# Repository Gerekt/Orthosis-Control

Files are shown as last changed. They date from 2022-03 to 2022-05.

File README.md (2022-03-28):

# Orthosis-Control
A Convolutional Neural Network powered control system for a hand orthosis/exoskeleton. 

This repository holds files related to a graduation assignment for the Saxion University of applied sciences.
The MSWC dataset is used in combination with the MobileNetV3 architecture for the CNN.

# Folder structure
The folders have the following purposes:

**Dataset**:                     Holds the dataset that is used. The dataset consits of certain parts/words of the MSWC dataset.

**On-device inference**:         Holds all the needed files for the inference that is used on the Raspberry Pi 4B. A trained model is also needed but not included

**Pre-processing&Training**:     Holds pre-processing scripts for the MSWC dataset and the notebook that is used for training the model.

**Trained models**:              Holds several pre-trained models.

# Setup guide
This guide will describe the process of running a pre-trained model onto a new Raspberry Pi 4B.
The following things are needed:
-Raspberry Pi 4B + USB-C power supply
-Minimum 16GB of storage, so either a flashdrive or SD card(Flashdrive preffered due to read-write cycles damaging SD card)
-Mini displayport -> HDMI/Displayport cable
-IQaudio Codec Zero ADC HAT
-Secondary monitor + Keyboard + Mouse for RPI

**Flashing image to Raspberry Pi**
We start by flashing an image which holds an OS to the Raspberry Pi. We will use an existing image which includes the TensorFlow library, which will make instalation easier.

Download the QEngineering 64-bit Raspberry Pi OS image: https://drive.google.com/file/d/1s8ulI44O96qmVPmWyz8yw3lzamh-32gN/view?usp=sharing

Download and install the image flasher: https://downloads.raspberrypi.org/imager/imager_latest.exe

Insert the storage device into your computer
Open the Raspberry Pi imager
Go to: Select OS, and scroll down and select the custom image file.



Select the recently downloaded QEngineering Raspberry Pi OS image, and press Open.

Lastly select the right storage device(which should be the inserted SD or flashdrive), and press the write button in the imager. 

Let the process finish, which will result in a flashed storage device.

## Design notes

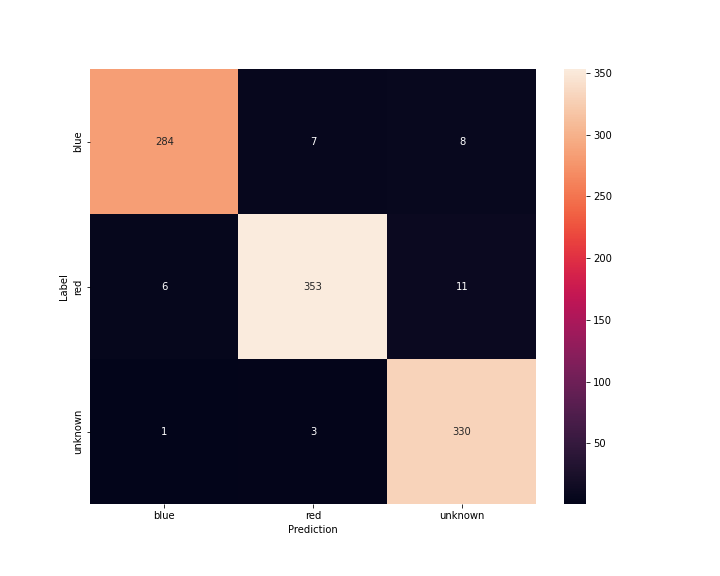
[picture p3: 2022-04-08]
Trained models/V5.0_simpleCNN_MSWC_blue-red-unknown_spectrogram_05-04-2022/metadata/confusion_matrix.png

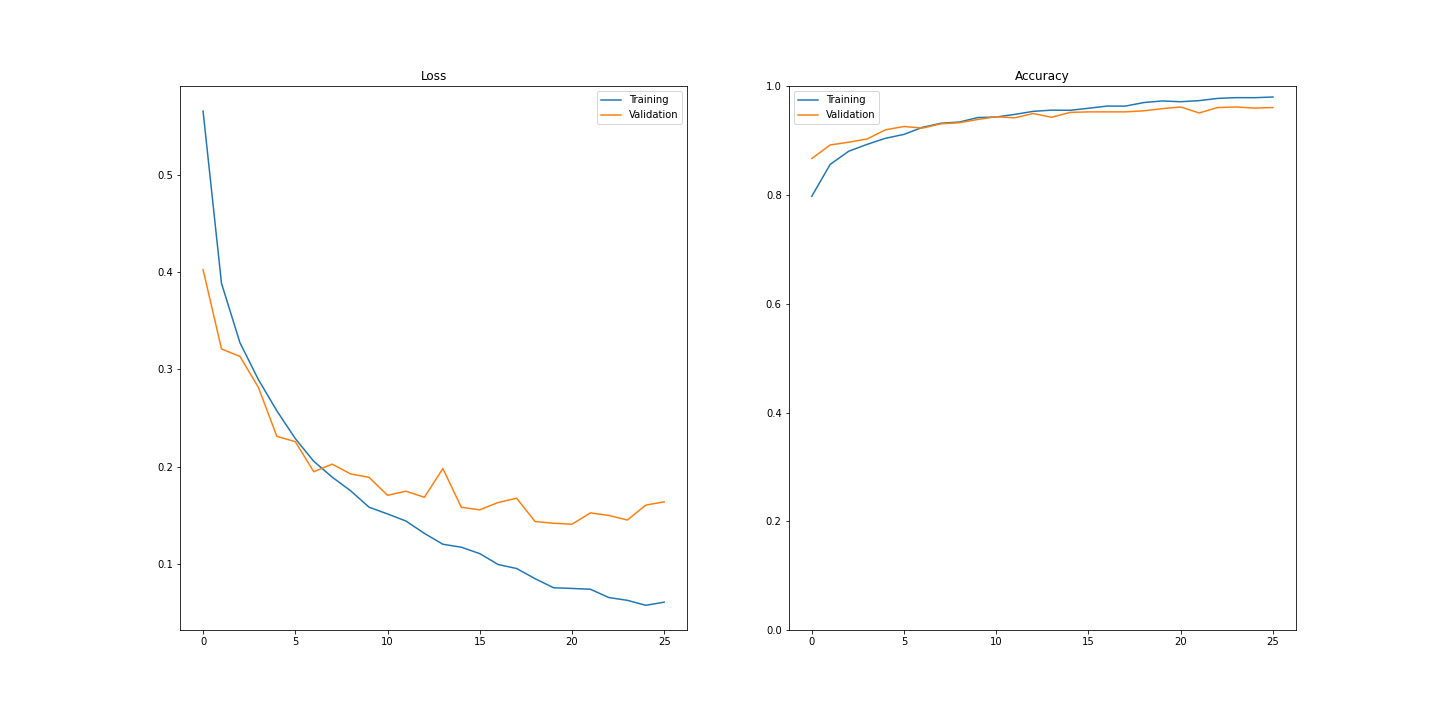
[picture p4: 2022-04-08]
Trained models/V5.0_simpleCNN_MSWC_blue-red-unknown_spectrogram_05-04-2022/metadata/training_graph.png

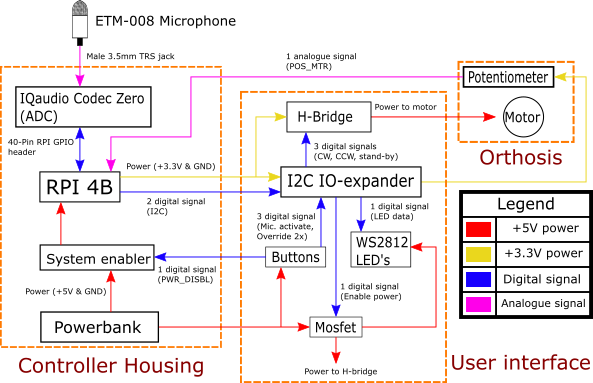
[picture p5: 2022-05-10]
Construction Files/Diagrams/Electronic Diagram(Technical).png

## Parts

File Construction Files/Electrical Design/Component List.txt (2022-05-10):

-------------------------------------------------------------------------------------------------------------
Nog te kopen

1x 3-pos, aan-neutraal-uit tuimelschakelaar: https://www.robotshop.com/be/nl/momentary-manual-dpdt-tuimelschakelaar.html
1x 2-pos, aan-uit tuimelschakelaar: https://www.kiwi-electronics.nl/nl/aan-uit-tuimelschakelaar-rood-3630?search=rocker
1x Drukknop met LED: https://www.kiwi-electronics.nl/nl/16mm-drukknop-met-led-puls-groen-2179
1x5 WS2812B 5mm LED's, 3 daadwerkelijk nodig: https://opencircuit.shop/product/NeoPixel-Diffused-5mm-Through-Hole-LED
3x LED Panel Houder/mount: https://www.tinytronics.nl/shop/nl/componenten/led's/accessoires/5mm-led-houder-metaal

1x TB6612 H-Bridge: https://www.kiwi-electronics.nl/nl/adafruit-tb6612-1-2a-dc-stepper-motor-driver-breakout-board-2188
1x I2C IO expander: https://www.tinytronics.nl/shop/nl/communicatie-en-signalen/io-converters/pcf8574-i2c-io-expander

3x Transistor NPN(general purpose): https://www.tinytronics.nl/shop/nl/componenten/transistoren/npn-transistor-2n3904 
2x Transistor MOSFET-N (Toggle power + motor/LEDS):https://www.kiwi-electronics.nl/nl/n-channel-power-mosfet-irlb8721-397?search=mosfet
8x Resistors (1x 5K, 3x 1K, 1x 10K, 1x 100, 2x 500): -
3x Diode: https://www.tinytronics.nl/shop/nl/componenten/diodes/diode-1n4007
2x Capacitor(Decouple): https://www.tinytronics.nl/shop/nl/componenten/condensatoren/100nf-50v-ceramische-condensator

1x Powerbank, elke powerbank >10.000mAH en meerdere poorten goed: https://www.mediamarkt.nl/nl/product/_hama-187261a-power-pack-pd10-hd-antraciet-1714846.html
1x Connector GX12-5 5-pin M+F: https://www.tinytronics.nl/shop/nl/kabels-en-connectoren/connectoren/gx/gx12/gx12-5-connector-set

2x1m Cable sleeve(To bundle outgoing cables), kon het niet vinden bij de andere winkels:https://nl.rs-online.com/web/p/cable-sleeves/0408209 
											https://www.123-3d.nl/123-3D-Vlechtkous-4-mm-zwart-1-meter-i5043-t13165.html
											 
1x Type C connector oplaad poort: https://opencircuit.shop/product/usb-2.0-type-c-connector-breakout-board
2x USB-C to loose wire stroomkabel(Powerbank -> oplaadpoort, Relay -> RPI): https://www.tinytronics.nl/shop/nl/kabels-en-connectoren/kabels-en-adapters/usb/usb-c/usb-c-stroomkabel-met-losse-draden-en-hoek-30cm?sort=p.price&order=ASC
2x USB-A Male connector(Output powerbank): https://www.tinytronics.nl/shop/nl/kabels-en-connectoren/connectoren/usb/usb-a-connector-diy-male

1x Raspberry Pi 4b(Gebruik nu eigen RPI): 
-------------------------------------------------------------------------------------------------------------
Al gekocht

1x Minimaal 16 GB storage (USB flashdrive(betere levensduur) of sd kaart(minder stroomverbruik))
1x IQaudIO CODEC Zero
1x ETM-008 Uni-directional microphone

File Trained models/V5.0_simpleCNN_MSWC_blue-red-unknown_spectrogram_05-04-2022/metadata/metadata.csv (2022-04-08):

ModelName | Test split accuracy | CNN | Dataset | TF_Version | Data augmentation percentage | Time shift percentage | Noise addition percentage | Noise SNR | Normalize Spectrogram | Sample Rate | Window length(Spectro) | Hop length(Spectro) | NFFT size | Epochs | Batch size | Comments
V5.0_simpleCNN_MSWC_blue-red-unknown_spectrogram_05-04-2022 | 0.9641076769690927 | simpleCNN | MSWC | 2.8.0 | 0.25 | 0.5 | 0.3 | 10 | False | 16000 | 256 | 128 | 256 | 60 | 64 | Normal 1D spectrogram 129x124, from_logits=True in sparsecatagoricalAccuracy

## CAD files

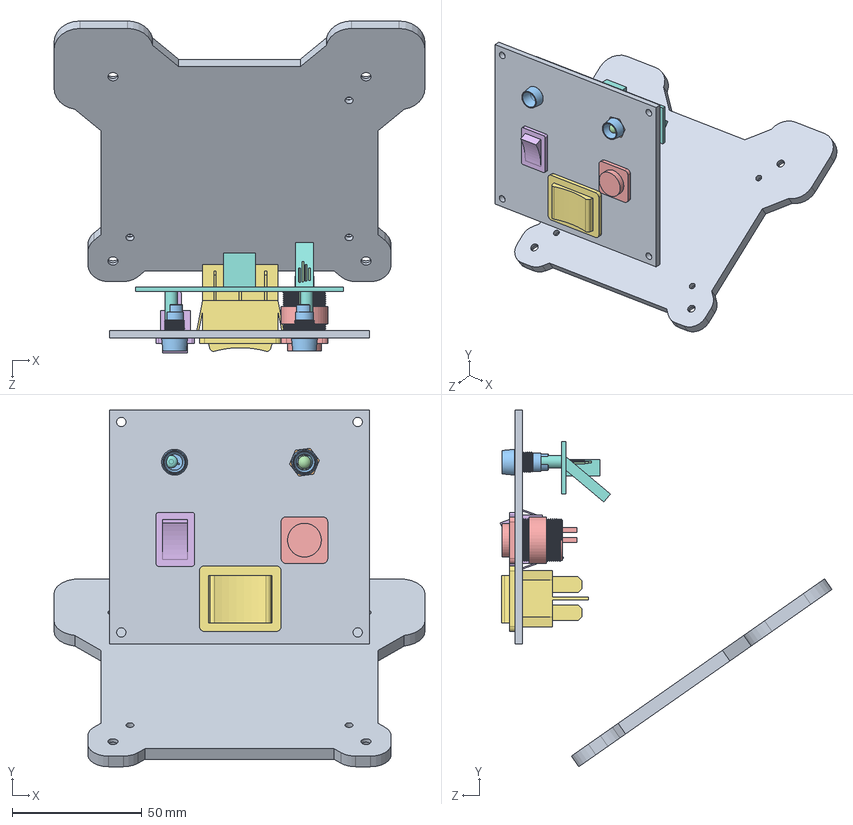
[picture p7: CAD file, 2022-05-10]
Construction Files/CAD/User Interface Panel + Walls.SLDASM
142.8 x 137.2 x 127.8 mm
Enclosure Interface panel FRONT
GrundkÃ¶rper v7.iges x 2
16mm Push Button Kiwi
RockerSwitch On_Off Kiwi
Double Throw Rocker Switch Forward_off_Backward
LED interface board
Enclosure User Interface Base

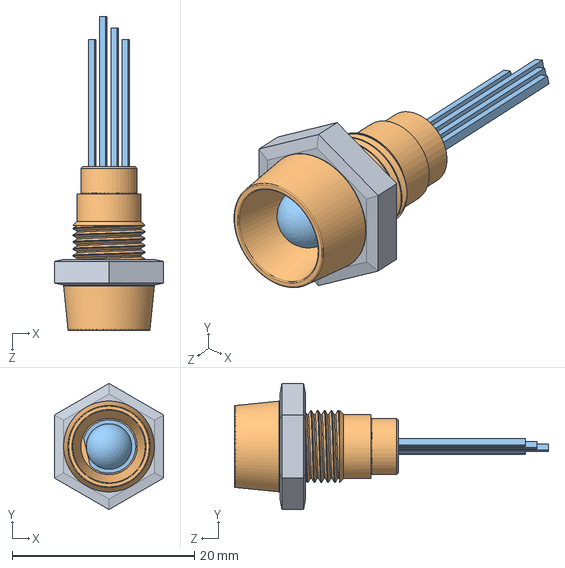
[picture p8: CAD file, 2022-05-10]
Construction Files/CAD/Components/LED holder 5mm.SLDASM
12.0 x 13.9 x 34.5 mm
GrundkÃ¶rper v7.iges
5mm RGB LED

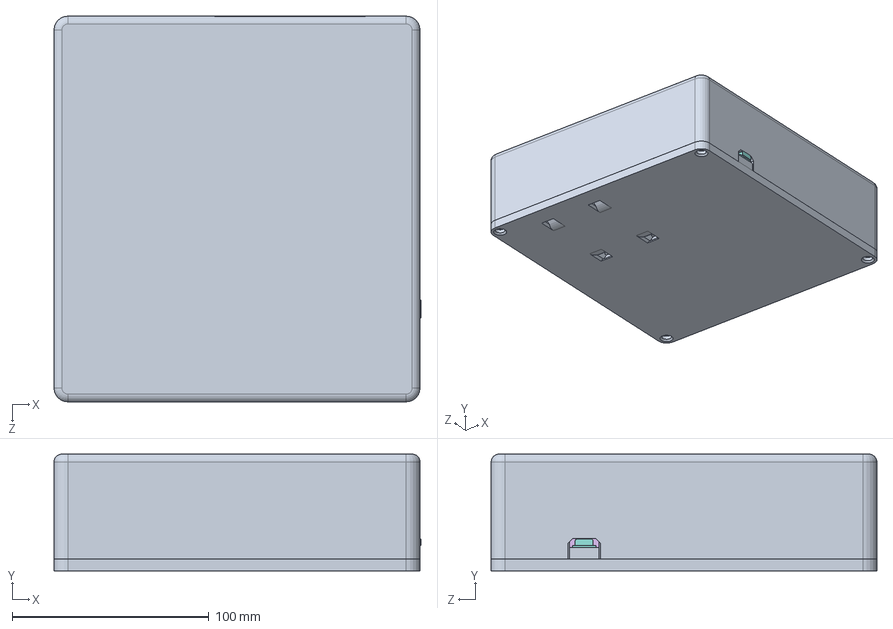
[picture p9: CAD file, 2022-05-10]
Construction Files/CAD/Control system enclosure.SLDASM
186.5 x 59.4 x 196.0 mm
Control system enclosure Base
PCB, RPi4ModelB
Broadcom BCM2711B0 CPU, RPi4ModelB
2.54 mm DUPONT MALE PIN HEADER, POE, 2X2, RPi4ModelB
2.54 mm DUPONT MALE PIN HEADER, IO, 2X20, RPi4ModelB
Camera Connector, RPi4ModelB
Microphone Plug, RPi4ModelB
Display Connector, RPi4ModelB
Gigabit Ethernet Port, RPi4ModelB
Female Micro HDMI Connector, RPi4ModelB x 2
Female USB Type C Connector, RPi4ModelB
2X USB3.0 PORTS, RPi4ModelB
91D77 D9WHV 778K, 4 GB LPDDR4 SDRAM, RPi4ModelB
Cypress CYW43455 Wireless Module Cover, RPi4ModelB
SD Card Slot, RPi4ModelB
VIA VL805 PCIe USB 3.0 controller, RPi4ModelB
2X USB2.0 PORTS, RPi4ModelB
Broadcom BCM54213PE Gigabit Ethernet Transceiver, RPi4ModelB
MxL7704 Universal PMIC, RPi4ModelB
heat2 x 2
heat4
Hama PD10-HD powerbank
System enabler board
USB-C port
Control system enclosure Top

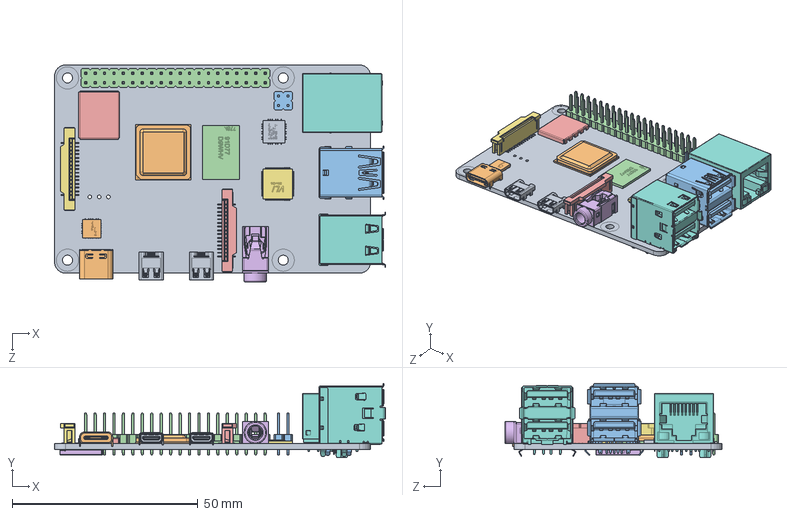
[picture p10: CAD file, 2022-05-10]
Construction Files/CAD/Components/Raspberry Pi 4b/Raspberry Pi 4 Model B.SLDASM
89.0 x 19.9 x 58.4 mm
PCB, RPi4ModelB
Broadcom BCM2711B0 CPU, RPi4ModelB
2.54 mm DUPONT MALE PIN HEADER, POE, 2X2, RPi4ModelB
2.54 mm DUPONT MALE PIN HEADER, IO, 2X20, RPi4ModelB
Camera Connector, RPi4ModelB
Microphone Plug, RPi4ModelB
Display Connector, RPi4ModelB
Gigabit Ethernet Port, RPi4ModelB
Female Micro HDMI Connector, RPi4ModelB x 2
Female USB Type C Connector, RPi4ModelB
2X USB3.0 PORTS, RPi4ModelB
91D77 D9WHV 778K, 4 GB LPDDR4 SDRAM, RPi4ModelB
Cypress CYW43455 Wireless Module Cover, RPi4ModelB
SD Card Slot, RPi4ModelB
VIA VL805 PCIe USB 3.0 controller, RPi4ModelB
2X USB2.0 PORTS, RPi4ModelB
Broadcom BCM54213PE Gigabit Ethernet Transceiver, RPi4ModelB
MxL7704 Universal PMIC, RPi4ModelB

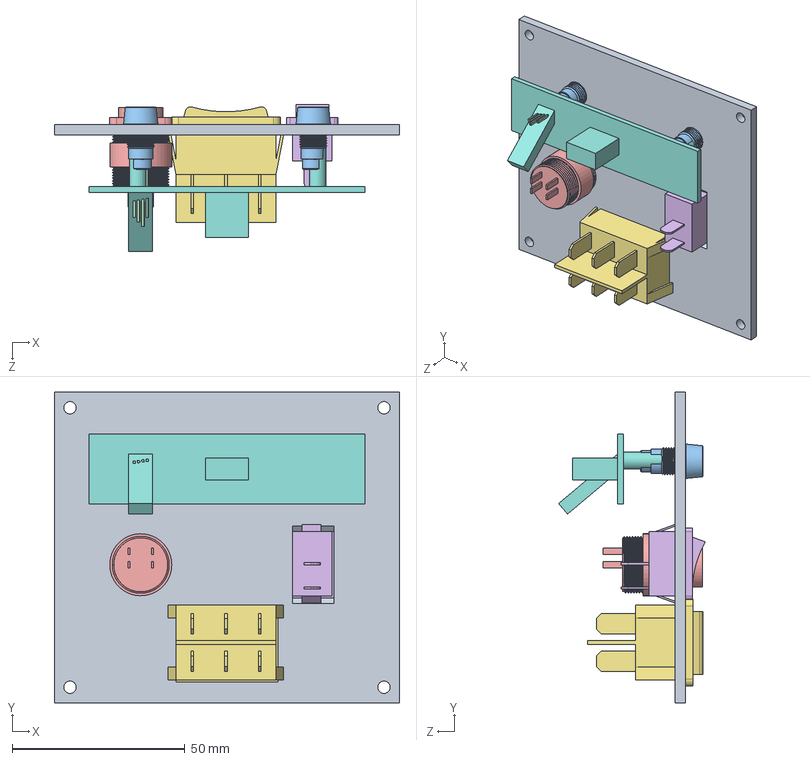
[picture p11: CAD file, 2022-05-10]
Construction Files/CAD/User interface Assembly.SLDASM
100.0 x 90.0 x 42.5 mm
Enclosure Interface panel FRONT
GrundkÃ¶rper v7.iges x 2
16mm Push Button Kiwi
RockerSwitch On_Off Kiwi
Double Throw Rocker Switch Forward_off_Backward
LED interface board

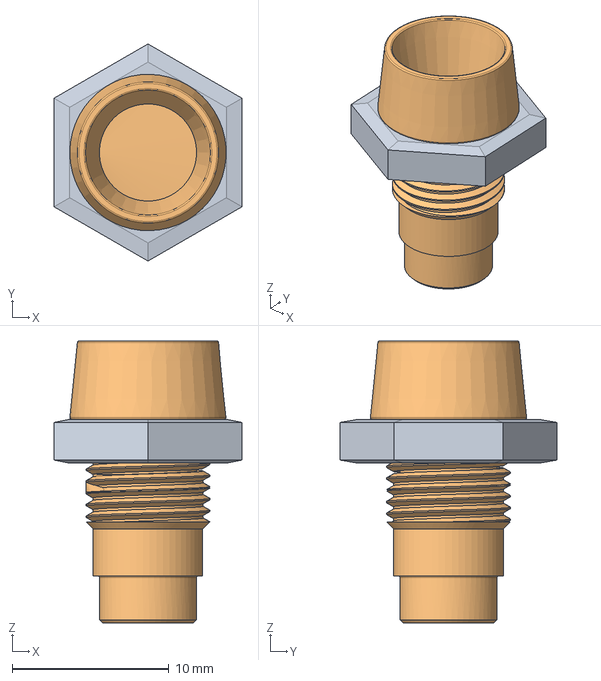
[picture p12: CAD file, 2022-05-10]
Construction Files/CAD/Components/5mm LED holder/LED holder 5mm.step
12.0 x 13.9 x 18.0 mm
M8 Kontermutter
Grundkörper

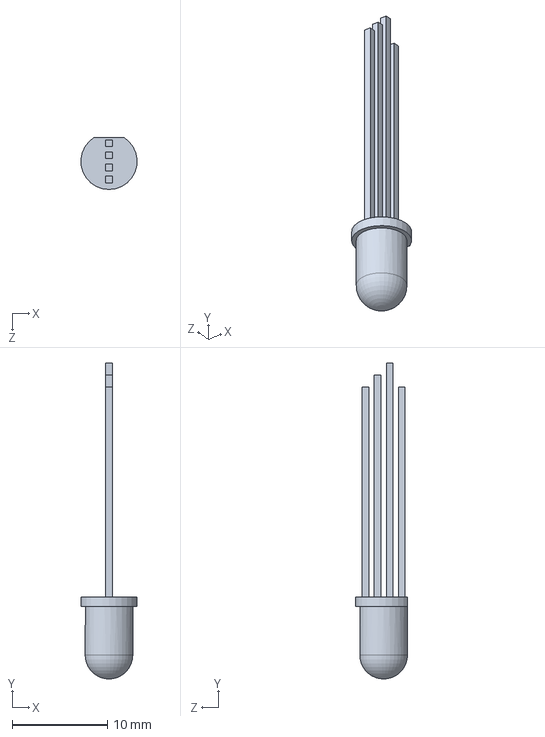
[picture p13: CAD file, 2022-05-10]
Construction Files/CAD/Components/5mm RGB LED.SLDPRT
5.88 x 33.1 x 5.45 mm

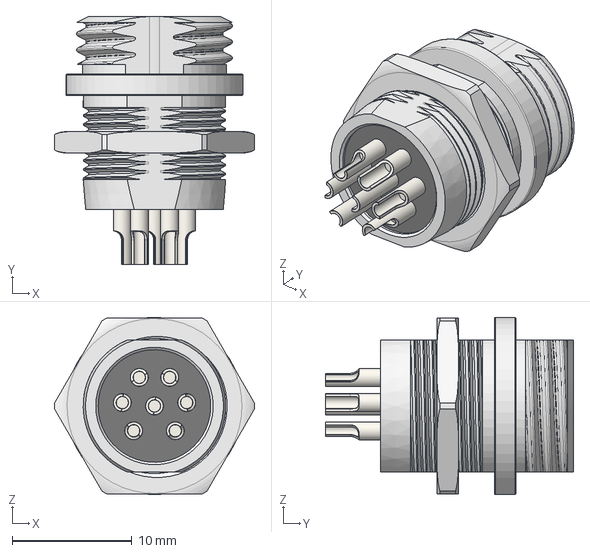
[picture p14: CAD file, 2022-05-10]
Construction Files/CAD/Components/GX-12 Connector/GX12-7P v2.step
16.7 x 20.7 x 14.8 mm

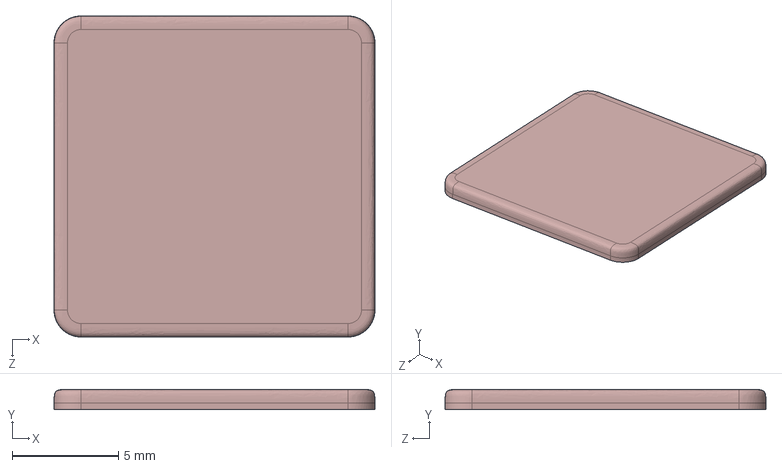
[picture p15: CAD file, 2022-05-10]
Construction Files/CAD/Components/Heatsink RPI/heat3.STEP
15.1 x 0.953 x 15.1 mm

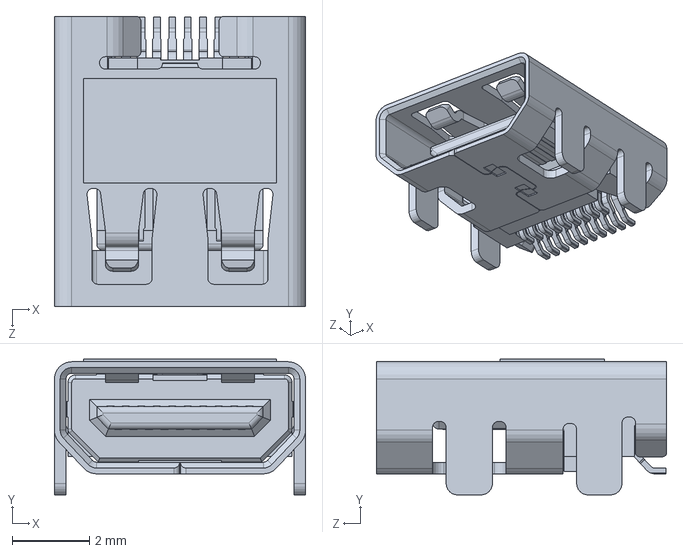
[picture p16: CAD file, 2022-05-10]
Construction Files/CAD/Components/Raspberry Pi 4b/Female Micro HDMI Connector, RPi4ModelB.SLDPRT
6.50 x 3.52 x 7.50 mm

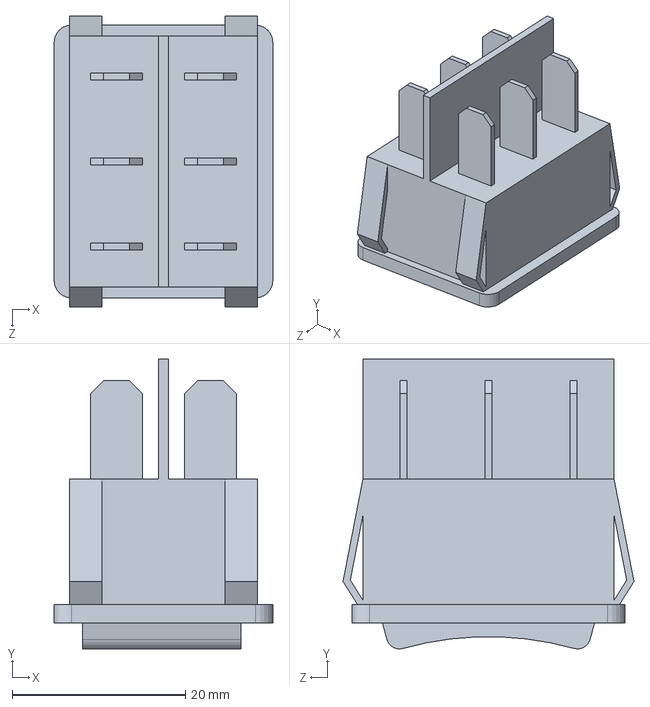
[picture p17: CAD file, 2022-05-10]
Construction Files/CAD/Components/Double Throw Rocker Switch Forward_off_Backward.SLDPRT
25.2 x 33.5 x 33.6 mm

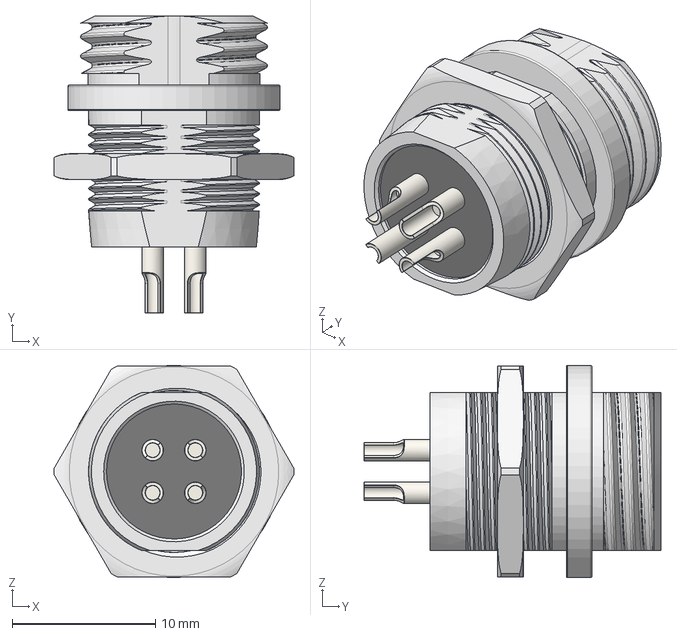
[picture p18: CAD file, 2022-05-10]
Construction Files/CAD/Components/GX-12 Connector/GX12-4P v3.step
16.7 x 20.7 x 14.8 mm

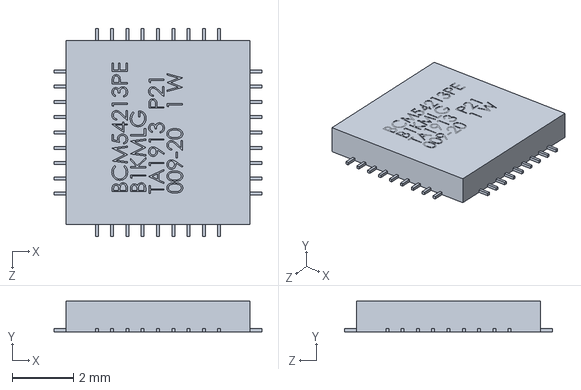
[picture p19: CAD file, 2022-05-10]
Construction Files/CAD/Components/Raspberry Pi 4b/Broadcom BCM54213PE Gigabit Ethernet Transceiver, RPi4ModelB.SLDPRT
6.80 x 1.00 x 6.80 mm

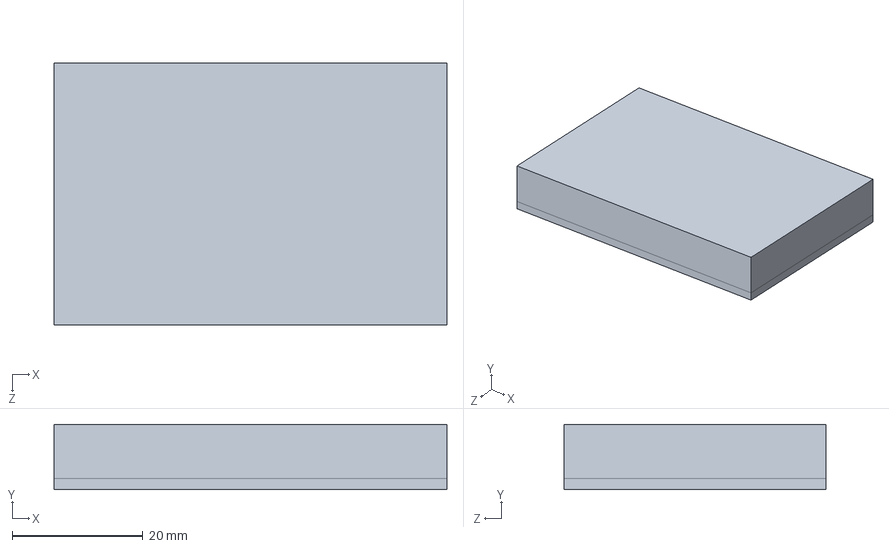
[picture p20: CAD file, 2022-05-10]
Construction Files/CAD/System enabler board.SLDPRT
60.1 x 10.0 x 40.1 mm

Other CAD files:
Construction Files/CAD/Components/GX-12 Connector/GX12-6P v2.step
Construction Files/CAD/Components/Raspberry Pi 4b/2.54 mm DUPONT MALE PIN HEADER, IO, 2X20, RPi4ModelB.SLDPRT
Construction Files/CAD/Components/16mm Push Button Kiwi.SLDPRT
Construction Files/CAD/Components/5mm LED holder/LED holder 5mm.iges
Construction Files/CAD/Components/GX-12 Connector/GX12-2P v2.f3d
Construction Files/CAD/Components/GX-12 Connector/GX12-2P v2.iges
Construction Files/CAD/Components/GX-12 Connector/GX12-2P v2.step
Construction Files/CAD/Components/GX-12 Connector/GX12-3P v2.f3d
Construction Files/CAD/Components/GX-12 Connector/GX12-3P v3.iges
Construction Files/CAD/Components/GX-12 Connector/GX12-3P v3.step
Construction Files/CAD/Components/GX-12 Connector/GX12-4P v3.f3d
Construction Files/CAD/Components/GX-12 Connector/GX12-4P v3.iges
Construction Files/CAD/Components/GX-12 Connector/GX12-5P v2.f3d
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

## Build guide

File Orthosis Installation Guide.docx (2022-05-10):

# iOrthosis-Control

A Convolutional Neural Network powered mobile control system for a hand orthosis/exoskeleton activated by voice commands. All running on a Raspberry Pi 4B.

This repository holds files related to a graduation assignment for the Saxion University of applied sciences. The MSWC dataset is used in combination with a simple CNN architecture.

# Folder structure

The folders have the following purposes:

Construction Files: Folder containing CAD files and electronic diagrams.

Custom dataset: Custom dataset containing several wavs of environmental sounds and conversations. Can be used to test the model after training. Additional wavs may also be added, although they need to be 16kHz .WAV files

Dataset MSWC: A pre-processed dataset containing the words: “red”& “blue”. The words are derived from selected words of the MSWC dataset. Link to entire dataset (https://mlcommons.org/en/multilingual-spoken-words/)

On-device inference: Holds all the needed files for the inference that is used on the Raspberry Pi 4B. A trained model is also needed for inference which is not included in this folder.

Pre-processing&Training: Holds pre-processing scripts for the MSWC dataset(MSWC_ds_PreProc) and the notebook that is used for training the model(modelTraining_ControlSystem). The opusdec.exe is also needed for the pre-processing of the dataset.

Trained models: Holds several pre-trained models. From V5.0 onwards the models also contain their performance data and metadata. This can be found inside of the model folder under “metadata” & “custom_dataset_results”. Currently V5.0 is meant to be used with the provided inference scripts. This model has one issue that it misclassifies silences as commands, due to no silences being included in the training.

# Setup RPI image

This guide will describe the process of running a pre-trained model onto a new Raspberry Pi 4B. The following things are needed:

- Raspberry Pi 4B + USB-C power supply
- Minimum 16GB of storage, so either a flashdrive or SD card(Flashdrive preferred due to read-write cycles damaging SD card)
- Mini displayport -> HDMI/Displayport cable
- IQaudio Codec Zero ADC HAT or another ADC for the microphone
- Secondary monitor + Keyboard + Mouse for RPI

Flashing image to Raspberry Pi We start by flashing an image which holds an OS to the Raspberry Pi. We will use an existing image which includes the TensorFlow library, which will make installation easier.

Download the QEngineering 64-bit Raspberry Pi OS image: https://drive.google.com/file/d/1s8ulI44O96qmVPmWyz8yw3lzamh-32gN/view?usp=sharing

or their GitHub: https://github.com/Qengineering/RPi-image

Download and install the image flasher:

https://downloads.raspberrypi.org/imager/imager_latest.exe

Insert the storage device into your computer. Open the Raspberry Pi imager, Go to: Select OS, and scroll down and select the custom image file.

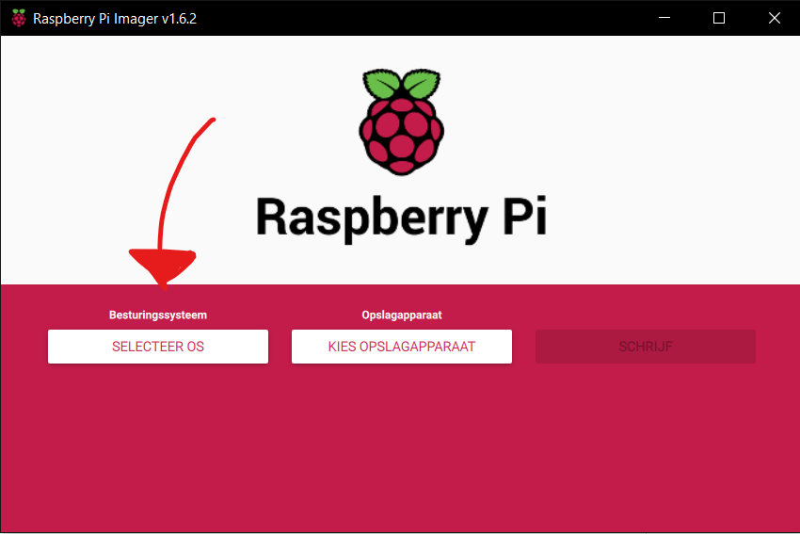
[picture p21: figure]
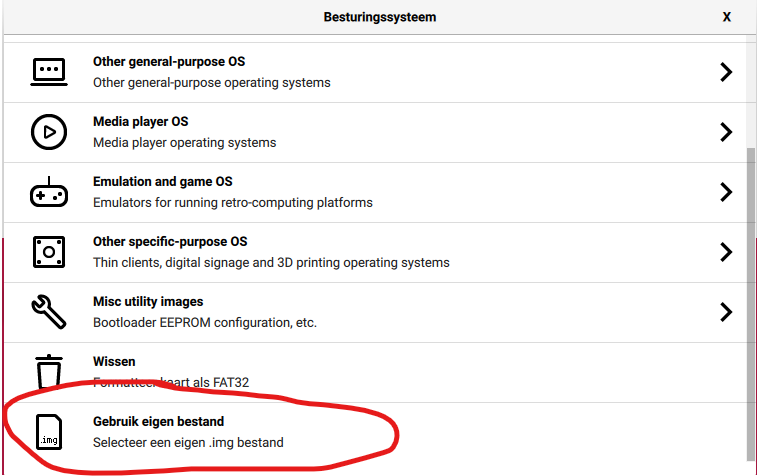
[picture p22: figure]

Select the recently downloaded QEngineering Raspberry Pi OS image, and press Open.

Select the right storage device(which should be the inserted SD or flashdrive).

Before flashing also press the cog icon after you have selected the OS file and storage device.

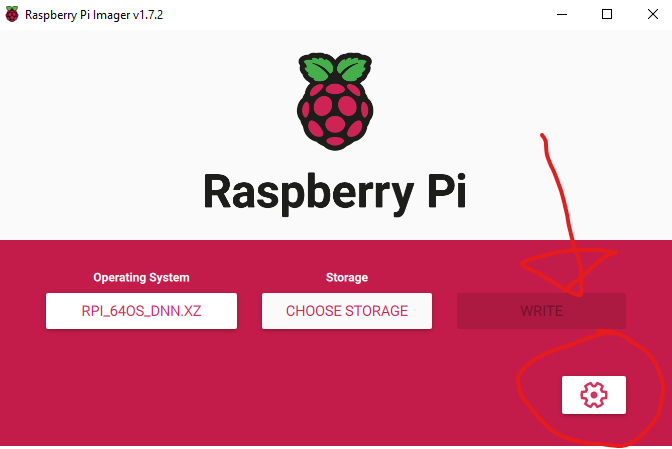
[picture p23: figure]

It will open up another window which allows the user to configure certain settings so that they do not need to be changed after flashing.

The hostname can be set to any hostname that is required, here I used “orthosis.local”, that means it can be found in the local network using that name.

SSH is also enabled, this will allow for accessing the raspberry pi using another computer and a program called Putty. You can then access the RPI via a terminal.

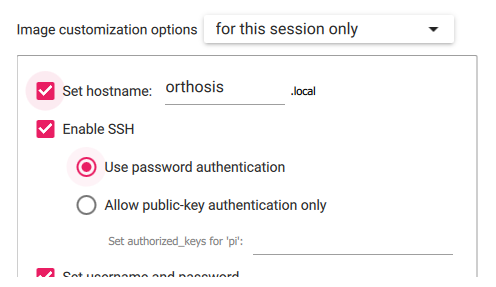
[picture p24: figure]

The password and username is also set. The password is currently set to “hankamp”.

The WiFi network is also configured. The name of the network needs to go at SSID. The password of the network should be entered at the password section.

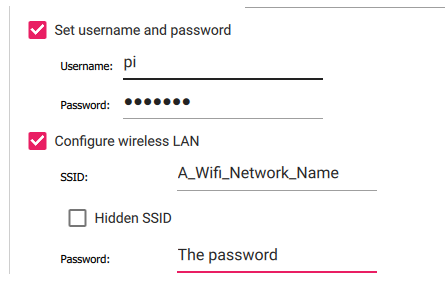
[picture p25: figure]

Lastly the locale settings need to be configured aswell. This ensures the right timezone and wifi settings. Here I used NL LAN county and Amsterdam timezone.

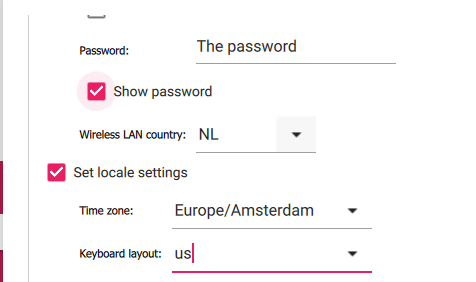
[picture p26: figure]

After the configuration press save, double check that you have the right storage device and press write.

This process might take a while.

Afterwards the SD card is flashed. Windows might ask if you want to reformat the drive. Do NOT do this, as it delete all the progress that is made thusfar.

# Putty guide

Instead of accessing the RPI by using a second monitor and peripherals. One can also access the RPI by using their main laptop/desktop. This can be done via SSH and a program called Putty. This will allow you to use your main computer for inputting commands to the RPI. This is not needed but may be more convenient.

You can download Putty here: https://www.chiark.greenend.org.uk/~sgtatham/putty/latest.html

Download and install the latest putty version for your machine.

After installing open putty, it will look similar to this.

For the hostname enter the hostname that was set during the configuration, so in my case that would be “orthosis.local”. Also add the user that you would like to log on as. So in this case the username is “pi”. Therefor the hostname will be: pi@orthosis or may also be pi@orthosis.local.

Additionally the IP may also be found via the RPI itself by typing “ifconfig” in a command window, or by looking at the router and the connected devices.

Your laptop/desktop will have to be on the same network as the RPI. This network will have to be the same one that was set during the configuration during the previous steps.

Give this configuration a name at the saved sessions. And press Save, this will allow for easier future access. After saving the configuration the connection can be established by pressing open.

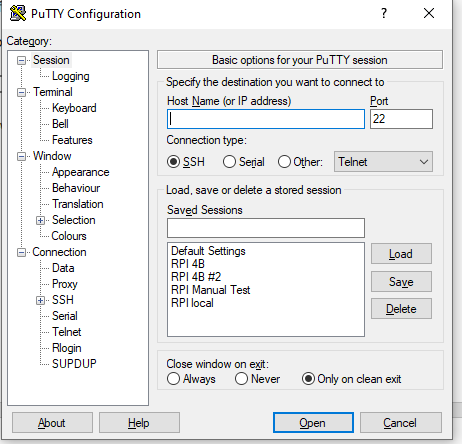
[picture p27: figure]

After opening the connection. Log in by using the password that was set, so “hankamp”. Now you can access the RPI via the command line terminal.

# Setup RPI settings

After flashing, the storage device can be inserted into the Raspberry Pi. Also connect the Raspberry to all the peripherals described in the previous chapter, such as the monitor. Also connect both HATs to the Raspberry Pi.

After connecting the peripherals connect the USB-C PSU to the Pi. Then login to the Raspberry Pi using the password: “3.14” or with “Hankamp” if the previous steps were followed.

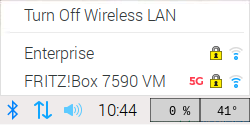
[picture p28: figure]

After logging in the Raspberry Pi will start up, this might take a while.

After starting the Raspberry Pi the WiFi may need to be manually enabled if this was not done correctly during the flashing of the SD card. To do this log in to the desired WiFi by clicking the symbol in the top right corner.

Press the button, after a while it shows the available networks, log into the desired network using the credentials.

Test if the WiFi has been correctly configured by opening the internet browser and going to a website.

If the Wi-Fi is set properly you can continue to the next step of the setup, which is needed for the HAT. Open a command prompt (Via SSH and Putty, or via a window on the RPI) and type the following line: “sudo raspi-config”

It will open the following screen.

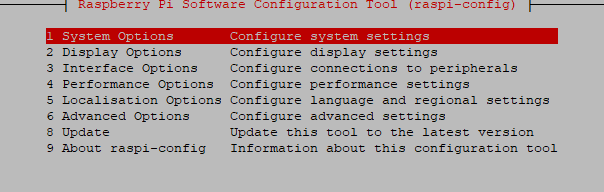
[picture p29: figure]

Go to interface (3) with the arrow keys and enable SPI and I2C by pressing enter. As can be seen on the following picture.

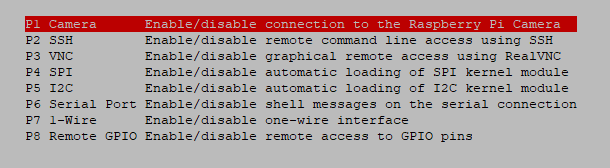
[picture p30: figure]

Now go back to the previous screen and go to the advance options (6). Then press enter on Expand Filesystem. This will make sure that the entire SD card is used for storage.

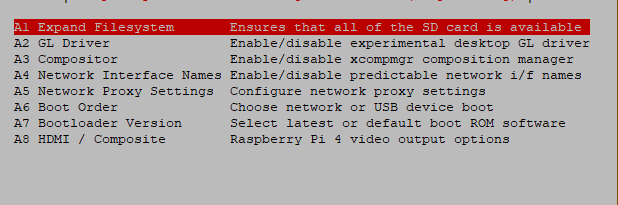
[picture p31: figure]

After this step go back to the previous screen and press finish. When asked to reboot press Yes. Otherwise type “sudo reboot now” Into the command line.

This will reboot the RPI and enable all the settings that were just configured.

Also update the current version by: “sudo apt-get update”

And “sudo apt-get upgrade” followed by “sudo reboot now”

After updating the settings, some additional settings need to be added for the HAT to work. This will be done by editing certain lines manually.

Type: “sudo nano ~/boot/config.txt”

Place an # before the line dtparam=audio=on, this will disable HDMI audio. Also add the following line under that one: “dtoverlay=iqaudio-codec”.

Save by pressing CTRL+X, and press enter.

# Cloning GitHub/Bitbucket repository

After configuring all the necessary settings, the code needs to be imported onto the Raspberry Pi. This will be done via Git. This step can only be completed if a working internet connection has been established on the RPI.

After the reboot that was done during the previous steps, log back into the RPI and open a new command line window.

Before being able to clone the repository you will need the link to the repository. Currently this is: https://github.com/Gerekt/Orthosis-Control.git

Now clone the repository by using the link.

Type: “sudo git clone https://github.com/Gerekt/Orthosis-Control.git”

The repository has now been cloned onto the RPI.

# Downloading Python libraries

The image that we used for the RPI already has several Python libraries pre-installed such as TensorFlow. However we need some additional libraries for the code.

First sounddevice: “python3 -m pip install sounddevice”

We cant install sounddevice easily as it needs portAudio to work, which is a C library. The only way to do this on a RPI with existing python modules is to manually compile the library with the following commands.

“cd ~” and “wget http://files.portaudio.com/archives/pa_stable_v190700_20210406.tgz”

“tar – xvzf pa_stable_v190700_20210406.tgz”

“sudo apt-get install libasound-dev”

“sudo apt-get install alsa-utils” And “sudo apt-get install mpg321”

“sudo apt-get install lame”

“cd portaudio” And “./configure && make”

“sudo make install” And “sudo ldconfig”

“sudo cp lib/.libs/libportaudio.a ~/Orthosis-Control/On-device inference/”

“sudo cp ~/portaudio/include/portaudio.h ~/Orthosis-Control/On-device\ inference/”

Now we have sounddevice and the C library. Next up Scipy. But first all the dependencies of scipy.

“sudo apt-get upgrade” and “sudo apt-get update”

“python3 -m pip install imutils” And “python3 -m pip install matplotlib”

“python3 -m pip install ipython” And “python3 -m pip install jupyter”

“python3 -m pip install sympy” and “python3 -m pip install nose”

Jupyter and Sympy may give errors when installing, during my installation this happened but did not matter for the installation of scipy.

“sudo apt install python3-gpiozero”

The last modules will take quite a long time, so be patient. (+20 min)

“python3 -m pip -vv install pandas” and “python3 -m pip -vv install numpy”

“python3 -m pip -vv install scipy”

# Testing configuration

Now we should have all the required libraries and files. We will test if everything is working by running the main control script. Go to it by: “cd ~/Orthosis-Control/On-device inference/”

And run the script with: “python3 ControlSystem.py”

After loading all the libraries it should start and give no library errors. It may give some errors related to the input device. This can be solved by running another script in the same folder. This script lists all the available input devices, the right one should be selected and copied into the main control system script.

Run the script with: “python3 audioListDevices.py”. The IQaudio microphone input should be the default.

Additional troubleshooting may be done with “arecord -l” and “arecord -L”, which lists all available devices.

And “sudo alsamixer”, which allows for changing certain parameters of the audio cards. Select the right card by pressing F6. Check if the microphones are enabled(Green box), if not enable or increase the gain by pressing “M” and the arrow keys respectively.

# Problems/Improvements

This chapter will summarize potential improvements that could be made and also the problems that the system currently has. If possible, solutions will also be provided that may solve the problem.

## Software

Problem | Type | Description | Solution
Models not trained with silences | Problem | The models are not trained with samples of silences and therefore misclassify silent audio as commands. | Add training silent training samples to unknown class or add new class containing silences and light noise.
Electronic peripherals not used | Improvement | The peripherals (LED’s, IO expander, and power button) are not used in the software | Add functionality into code.
Control script stops after 20sec | Improvement | The main script ControlSystem.py stops after 20sec. It stops as this made troubleshooting easier | Easier solution is to remove the 20 second variable in the loop to make it run indefinitely. May also add start stop capability to script, meaning that the classes get deleted and loaded again when the microphone activation button is pressed.
Device ID of IQAudio ADC can change | Improvement | The Device ID of the input devices of the IQAudio HAT can change after reboots. Which will result in no captured audio in the main control script. | Change HAT with USB ADC as the HAT is difficult to setup and troubleshoot. An USB ADC that is supported by the RPI may give better results.
TensorFlowLite capability | Improvement | The script currently uses the TensorFlow library and a TenserFlowLite model. This works fine but fully using TensorFlowLite as the library will give better performance. | Change TensorFlow library with TensorFlowLite. Will require slight reformatting of the code in the main script and wavToSpectrogram.py. Should be possible as no TensorFlow function is needed anymore.

## Mechanical

Problem | Type | Description | Solution
Sluggish case design | Improvement | The cases for the control system and user interface are big, bulky and heavy. They can be shrunk in size drastically. | Remodel both cases and print using less layers/walls. The models currently have a lot of empty space.
No aux passthrough | Improvement | The AUX cable from the microphone needs to go into the case, currently this results in a hole in the wall of the case. | Add an AUX passthrough where the user can plugin the microphone. The passthrough is fixed into the walls of the case. will then be connected to the ADC.
No analog inputs | Problem | The RPI does not have any analog inputs, but one is needed for the motor position | An I2C ADC can be added in the user interface, like for example the AD7992. Alternatively the motor position may be discarded, I.E. not be used.
Heat/cooling | Problem | The RPI gets very hot after a while. The HAT’s restrict airflow. | Add a special cooling case made of metal. A cooling fan may also be added. A sleeker HAT will also improve cooling.

## Electrical

Problem | Type | Description | Solution
System enabler | Improvement | System enabler is not implemented. System can therefor not be automatically shutdown | Select the right MOSFETS and rebuild the enabler board.
Cables | Improvement | Cables inbetween cases currently uses individual cables and are not long enough. | Rewire with cable with multiple strands like an ethernet cable.

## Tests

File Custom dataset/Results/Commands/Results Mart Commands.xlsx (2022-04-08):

MTestOG1(Quick) | Column1 | Column2 | Column3 | Column4 | Column5 | Column6 | Column7 | Column8 | Column9 | Column10 | Column11 | Column12 | Column13 | Column14 | Column15 | Column16 | Column17 | Column18 | Column19 | Column20 | Column21 | Column22 | Column23 | Column24 | Column25 | Column26 | Column27 | Column28 | Column29 | Column30 | Column31 | Column32 | Column33 | Column34 | Column35 | Column36 | Column37 | Column38 | Column39 | Column40 | Column41 | Column42 | Column43 | Column44 | Column45 | Column46 | Column47 | Column48 | Column49 | Column50 | Column51 | Column52 | Column53 | Column54 | Column55 | Column56 | Column57 | Column58 | Column59
Time of detected command(seconds): | 1.0 | 1.5 | 2.0 | 2.5 | 3.0 | 3.5 | 4.5 | 5.0 | 6.5 | 7.0 | 8.0 | 8.5 | 9.0 | 10.0 | 10.5 | 11.0 | 11.5 | 12.0 | 13.0 | 13.5 | 14.0 | 14.5 | 15.0 | 16.0 | 16.5 | 17.5 | 18.0 | 19.0 | 19.5 | 20.0 | 20.5 | 21.0 | 21.5 | 22.0 | 22.5 | 23.0 | 23.5 | 24.0 | 25.0 | 25.5 | 26.0 | 27.0 | 27.5 | 28.0 | 28.5 | 29.0 | 29.5 | 30.5 | 31.0 | 31.5 | 32.0 | 32.5 | 33.0 | 33.5 | 34.0 | 34.5 | 35.5 | 36.0 | 36.5
Detected command: | red | blue | blue | red | red | red | red | red | blue | blue | red | red | red | red | blue | blue | red | blue | blue | red | red | blue | blue | red | blue | red | blue | red | red | red | red | red | red | red | red | blue | red | blue | red | blue | red | red | blue | blue | blue | red | red | red | blue | blue | red | red | red | red | blue | blue | blue | blue | red
MTestOG2(Slow) | Column2 | Column3 | Column4 | Column5 | Column6 | Column7 | Column8 | Column9 | Column10 | Column11 | Column12 | Column13 | Column14 | Column15 | Column16 | Column17 | Column18 | Column19 | Column20 | Column21 | Column22 | Column23 | Column24 | Column25 | Column26 | Column27 | Column28 | Column29 | Column30 | Column31 | Column32 | Column33 | Column34 | Column35 | Column36 | Column37 | Column38 | Column39 | Column40 | Column41 | Column42 | Column43 | Column44 | Column45 | Column46 | Column47
Time of detected command(seconds): | 1.0 | 1.5 | 2.0 | 2.5 | 3.0 | 3.5 | 4.0 | 5.0 | 5.5 | 6.0 | 6.5 | 7.0 | 7.5 | 8.0 | 8.5 | 9.0 | 9.5 | 10.0 | 10.5 | 11.0 | 11.5 | 12.0 | 12.5 | 13.0 | 13.5 | 14.0 | 14.5 | 15.0 | 15.5 | 16.0 | 16.5 | 17.0 | 17.5 | 18.0 | 18.5 | 19.0 | 20.0 | 20.5 | 21.0 | 21.5 | 22.0 | 23.0 | 23.5 | 24.0 | 25.5 | 26.0
Detected command: | blue | blue | blue | blue | blue | red | blue | blue | red | blue | red | red | red | blue | blue | blue | red | red | red | blue | blue | blue | red | blue | red | blue | blue | red | red | blue | red | red | red | blue | red | red | blue | blue | blue | red | blue | blue | red | red | red | blue
MTest1(Quick) | Column2 | Column3 | Column4 | Column5 | Column6 | Column7 | Column8 | Column9 | Column10 | Column11 | Column12 | Column13 | Column14 | Column15 | Column16 | Column17 | Column18 | Column19
Time of detected command(seconds): | 5.0 | 7.0 | 10.0 | 13.0 | 20.5 | 22.5 | 27.0 | 29.5 | 32.5 | 36.5 | 38.0 | 39.5 | 42.0 | 44.0 | 44.5 | 46.5 | 56.0 | 61.5
Detected command: | red | red | red | blue | blue | blue | red | red | red | red | red | blue | blue | red | red | red | red | red
Mtest2(Slow) | Column2 | Column3 | Column4 | Column5 | Column6 | Column7 | Column8 | Column9 | Column10 | Column11 | Column12 | Column13 | Column14 | Column15 | Column16 | Column17 | Column18 | Column19 | Column20 | Column21
Time of detected command(seconds): | 3.5 | 5.0 | 7.0 | 9.0 | 10.0 | 13.0 | 20.5 | 22.0 | 27.0 | 29.5 | 32.5 | 36.5 | 38.0 | 39.5 | 42.0 | 44.0 | 44.5 | 46.5 | 56.0 | 61.5
Detected command: | red | red | red | red | red | blue | blue | blue | red | red | red | red | red | blue | blue | red | red | red | red | red
Mtest3(Quick) | Column2 | Column3 | Column4 | Column5 | Column6 | Column7 | Column8 | Column9 | Column10 | Column11 | Column12 | Column13 | Column14
Time of detected command(seconds): | 5.5 | 20.5 | 22.5 | 29.5 | 32.5 | 36.5 | 38.0 | 42.0 | 44.0 | 44.5 | 46.5 | 56.0 | 61.5
Detected command: | blue | blue | blue | red | red | red | red | blue | red | red | red | red | red
True labels (Quick) | Column2 | Column3 | Column4 | Column5 | Column6 | Column7 | Column8 | Column9 | Column10 | Column11 | Column12 | Column13 | Column14 | Column15 | Column16 | Column17 | Column18 | Column19 | Column20 | Column21 | Column22 | Column23 | Column24 | Column25 | Column26 | Column27 | Column28 | Column29 | Column30 | Column31 | Column32 | Column33 | Column34
Start + stop command: | 3.1 | 4.4 | 5.9 | 7.2 | 8.5 | 11.5 | 13.2 | 14.6 | 16 | 17.6 | 19 | 20.4 | 21.9 | 23.4 | 24.9 | 26.2 | 28.9 | 30.3 | 31.8 | 33.4 | 34.8 | 36.1 | 37.5 | 39 | 40.2 | 41.7 | 43.9 | 46 | 48 | 50.3 | 52.2 | 55.2 | 58.7
Spoken command: | red | red | Blue | red | red | Blue | red | blue | blue | blue | red | red | red | blue | blue | red | red | blue | red | blue | blue | red | red | blue | blue | blue | red | red | blue | blue | red | red | blue
True labels (Slow) | Column2 | Column3 | Column4 | Column5 | Column6 | Column7 | Column8 | Column9
Start + stop command: | 3.5 | 6.3 | 9.4 | 12.4 | 15.4 | 18.5 | 21.4 | 23.6
Spoken command: | Blue | Red | red | Blue | Blue | red | Blue | Red
Mtest4(Slow) | Column2 | Column3 | Column4 | Column5 | Column6 | Column7 | Column8 | Column9 | Column10 | Column11 | Column12 | Column13 | Column14
Time of detected command(seconds): | 5.5 | 20.5 | 22.5 | 29.5 | 32.5 | 36.5 | 38.0 | 42.0 | 44.0 | 44.5 | 46.5 | 56.0 | 61.5
Detected command: | blue | blue | blue | red | red | red | red | blue | red | red | red | red | red
Mtest5(Quick) | Column2 | Column3 | Column4 | Column5 | Column6 | Column7 | Column8 | Column9 | Column10 | Column11 | Column12 | Column13 | Column14 | Column15 | Column16 | Column17 | Column18 | Column19 | Column20 | Column21 | Column22 | Column23 | Column24 | Column25 | Column26 | Column27 | Column28 | Column29 | Column30 | Column31 | Column32 | Column33 | Column34 | Column35
Time of detected command(seconds): | 3.5 | 4.5 | 5.0 | 7.0 | 8.0 | 9.0 | 10.0 | 13.0 | 15.0 | 16.0 | 22.0 | 27.0 | 29.0 | 29.5 | 30.5 | 32.5 | 33.5 | 34.0 | 36.5 | 37.5 | 38.0 | 39.0 | 39.5 | 42.0 | 44.0 | 44.5 | 46.0 | 46.5 | 48.5 | 52.5 | 53.0 | 56.0 | 56.5 | 61.5
Detected command: | red | red | red | red | red | red | red | blue | blue | blue | blue | red | red | red | red | red | red | blue | red | red | red | red | blue | blue | red | red | red | red | blue | red | red | red | red | red
Mtest6(Slow) | Column2 | Column3 | Column4 | Column5 | Column6 | Column7 | Column8 | Column9 | Column10 | Column11 | Column12 | Column13 | Column14 | Column15 | Column16 | Column17 | Column18 | Column19 | Column20 | Column21 | Column22 | Column23 | Column24 | Column25 | Column26 | Column27 | Column28 | Column29 | Column30 | Column31 | Column32 | Column33 | Column34 | Column35
Time of detected command(seconds): | 3.5 | 4.5 | 5.0 | 7.0 | 8.0 | 9.0 | 10.0 | 13.0 | 15.0 | 16.0 | 22.0 | 27.0 | 29.0 | 29.5 | 30.5 | 32.5 | 33.5 | 34.0 | 36.5 | 37.5 | 38.0 | 39.0 | 39.5 | 42.0 | 44.0 | 44.5 | 46.0 | 46.5 | 48.5 | 52.5 | 53.0 | 56.0 | 56.5 | 61.5
Detected command: | red | red | red | red | red | red | red | blue | blue | blue | blue | red | red | red | red | red | red | blue | red | red | red | red | blue | blue | red | red | red | red | blue | red | red | red | red | red
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

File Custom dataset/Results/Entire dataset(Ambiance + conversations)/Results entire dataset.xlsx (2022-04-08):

84391 | Column2 | Column3 | Column4 | Column5 | Column6 | Column7 | Column8 | Column9
Time of detected command(seconds): | 1.0 | 3.0 | 9.5 | 12.5 | 15.5 | 29.5 | 30.0 | 30.5
Detected command: | blue | red | red | red | blue | red | red | blue
86568 | Column2 | Column3 | Column4
Time of detected command(seconds): | 3.0 | 16.5 | 23.5
Detected command: | blue | blue | red
133095 | Column2 | Column3 | Column4 | Column5 | Column6
Time of detected command(seconds): | 78.0 | 121.0 | 134.5 | 163.0 | 178.0
Detected command: | red | red | red | red | blue
147849 | Column2 | Column3 | Column4 | Column5 | Column6 | Column7 | Column8 | Column9 | Column10 | Column11 | Column12 | Column13 | Column14 | Column15 | Column16 | Column17 | Column18 | Column19 | Column20 | Column21 | Column22 | Column23 | Column24 | Column25 | Column26 | Column27 | Column28 | Column29 | Column30 | Column31 | Column32 | Column33 | Column34 | Column35 | Column36 | Column37 | Column38 | Column39 | Column40 | Column41 | Column42 | Column43 | Column44 | Column45 | Column46 | Column47 | Column48 | Column49 | Column50 | Column51 | Column52 | Column53 | Column54 | Column55 | Column56 | Column57 | Column58 | Column59 | Column60
Time of detected command(seconds): | 1.0 | 1.5 | 2.0 | 2.5 | 3.0 | 3.5 | 13.5 | 23.0 | 31.0 | 38.0 | 41.5 | 47.0 | 48.0 | 54.5 | 55.0 | 55.5 | 56.0 | 56.5 | 59.0 | 59.5 | 60.0 | 61.0 | 61.5 | 62.0 | 62.5 | 64.0 | 65.5 | 66.0 | 71.0 | 72.5 | 76.0 | 78.5 | 79.0 | 83.0 | 92.5 | 103.0 | 107.0 | 108.5 | 111.5 | 114.5 | 115.0 | 115.5 | 117.5 | 118.0 | 118.5 | 120.0 | 123.5 | 127.0 | 127.5 | 128.0 | 128.5 | 130.0 | 130.5 | 138.0 | 140.5 | 147.0 | 149.0 | 153.0 | 156.5
Detected command: | blue | blue | blue | blue | blue | blue | red | red | red | blue | red | blue | red | red | blue | blue | blue | red | blue | blue | red | red | blue | blue | red | red | blue | red | red | red | red | red | red | red | red | blue | blue | blue | red | red | red | red | blue | red | red | red | blue | blue | blue | red | red | red | red | red | blue | red | blue | red | red
329158 | Column2 | Column3 | Column4 | Column5 | Column6 | Column7 | Column8 | Column9 | Column10 | Column11 | Column12 | Column13 | Column14 | Column15
Time of detected command(seconds): | 3.5 | 31.5 | 32.5 | 33.0 | 39.5 | 45.5 | 46.0 | 50.0 | 53.5 | 61.0 | 62.0 | 63.5 | 66.5 | 80.0
Detected command: | red | red | red | red | red | red | red | red | red | red | red | red | red | red
415161 | Column2 | Column3 | Column4 | Column5
Time of detected command(seconds): | 6.5 | 21.5 | 23.0 | 31.0
Detected command: | red | red | red | blue
533026 | Column2
Time of detected command(seconds)
Detected command
591105 | Column2 | Column3 | Column4 | Column5 | Column6 | Column7 | Column8 | Column9 | Column10 | Column11 | Column12 | Column13 | Column14 | Column15 | Column16 | Column17 | Column18 | Column19 | Column20 | Column21 | Column22 | Column23 | Column24 | Column25 | Column26 | Column27 | Column28 | Column29 | Column30 | Column31 | Column32 | Column33 | Column34 | Column35 | Column36 | Column37 | Column38 | Column39 | Column40 | Column41 | Column42 | Column43
Time of detected command(seconds): | 10.0 | 15.0 | 125.0 | 127.0 | 176.0 | 176.5 | 177.0 | 178.5 | 188.0 | 208.5 | 209.0 | 209.5 | 210.0 | 210.5 | 213.0 | 214.0 | 215.0 | 215.5 | 216.0 | 223.5 | 233.0 | 245.0 | 245.5 | 256.5 | 259.5 | 260.0 | 298.0 | 299.5 | 329.5 | 354.0 | 367.0 | 373.0 | 390.0 | 393.5 | 395.0 | 400.5 | 411.0 | 433.0 | 433.5 | 439.5 | 445.5 | 446.0
Detected command: | blue | blue | red | red | red | red | red | red | blue | red | red | red | red | red | red | red | red | red | red | red | red | red | red | red | red | red | red | red | red | red | red | red | red | red | red | red | red | red | red | red | red | red
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

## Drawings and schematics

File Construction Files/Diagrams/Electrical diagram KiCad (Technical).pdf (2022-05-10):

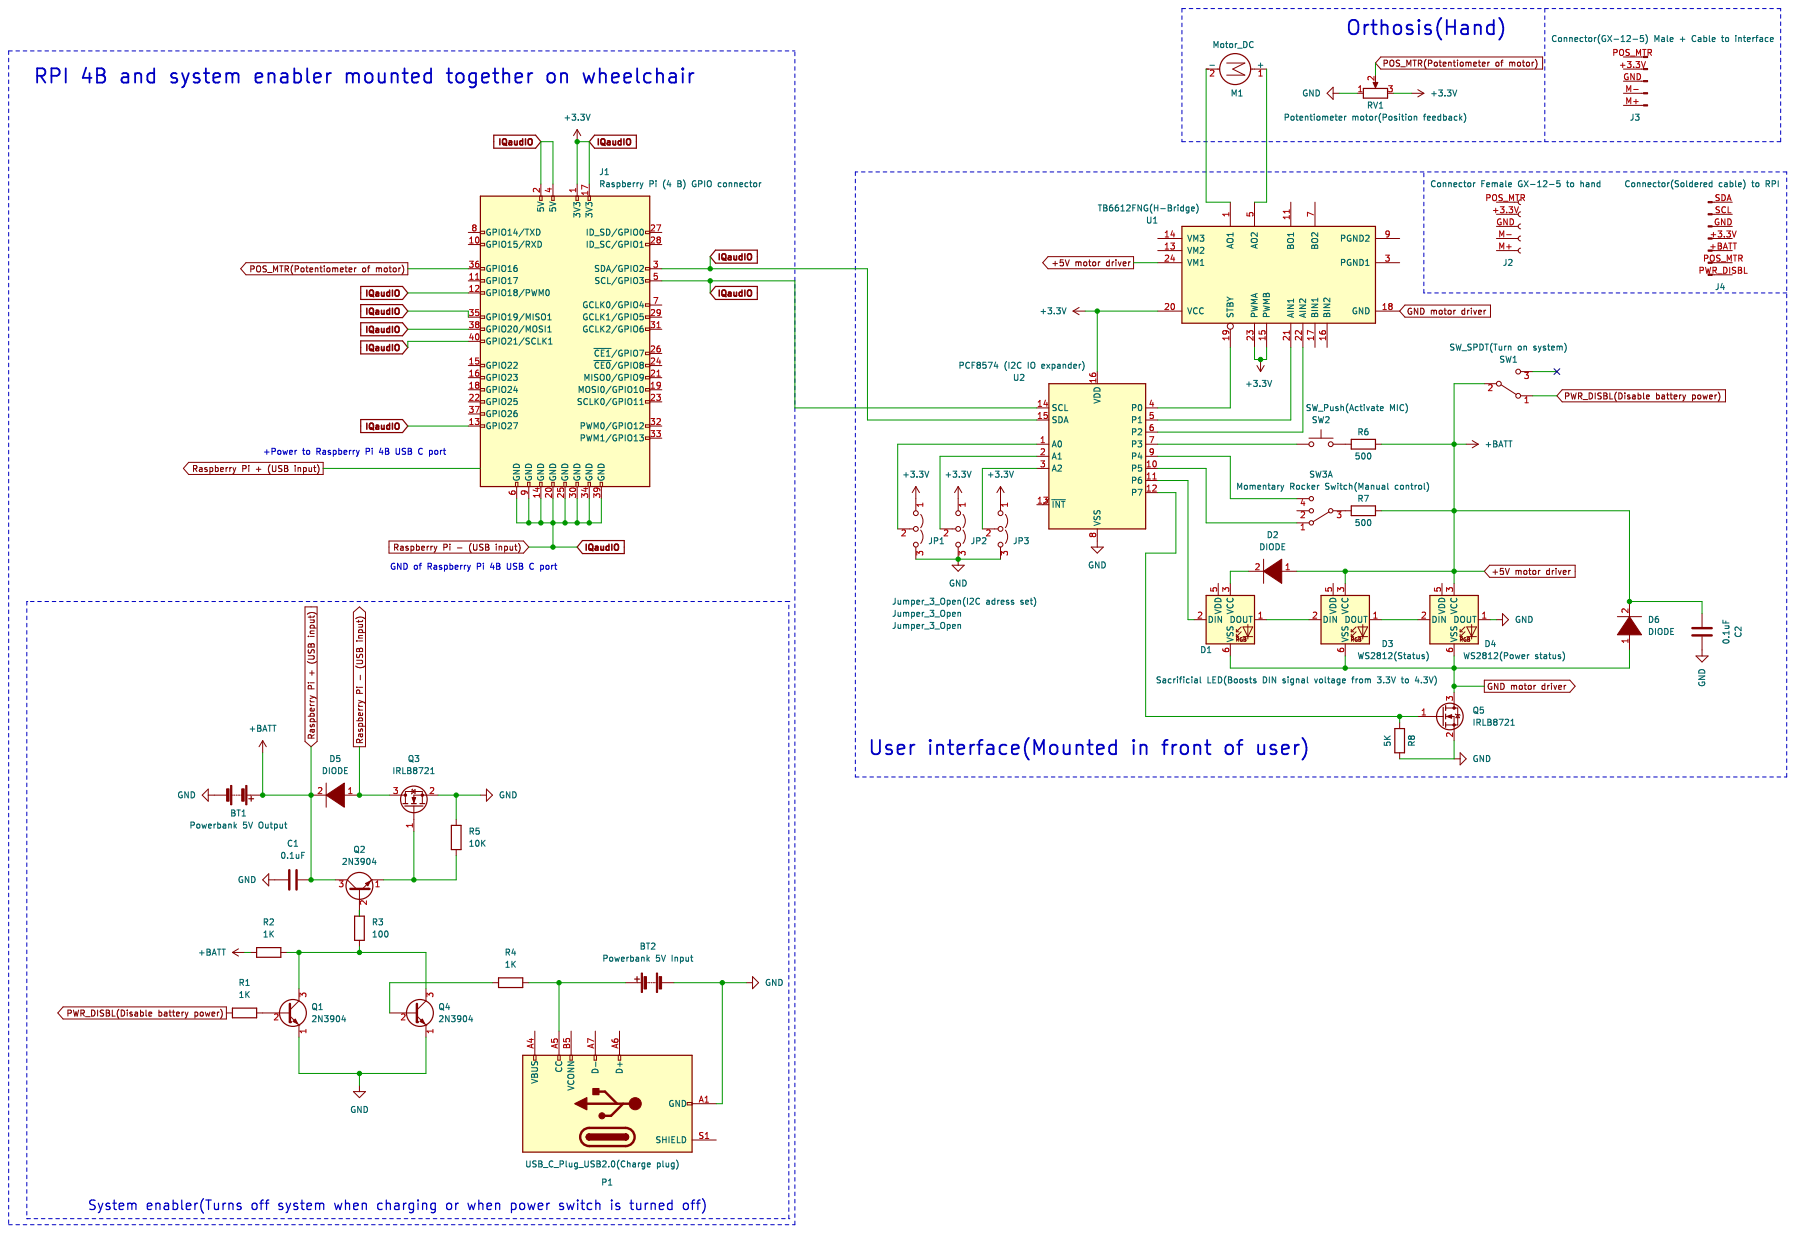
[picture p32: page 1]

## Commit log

2022-04-08 Changed folder structure, added new verion of training notebook that adds metadata to the saved model, added more comments in various scripts. Also added the custom dataset togheter with the results 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
    [133095_V5.0_simpleCNN_MSWC_blue-red-unknown_spectrogram_05-04-2022.csv, 147849_V5.0_simpleCNN_MSWC_blue-red-unknown_spectrogram_05-04-2022.csv, 329158_V5.0_sim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]
2022-05-10 Added motor controls
2022-05-10 Non code files added
    Added construction files(CAD models + diagrams) and the manual for the system
    [16mm Push Button Kiwi.SLDPRT, 2.54 mm DUPONT MALE PIN HEADER, IO, 2X20, RPi4ModelB.SLDPRT, 2.54 mm DUPONT MALE PIN HEADER, IO, 2X40, RPi4ModelB.SLDPRT, 2.54 mm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]
